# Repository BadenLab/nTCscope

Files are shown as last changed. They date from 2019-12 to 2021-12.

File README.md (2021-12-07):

<p align="right">
<h1 align="center">nTC(DBO)-Scope</h1></p>
<h4 align="center">An open source and ultra-low-cost design for large 3D field of view 2-photon microscopy</h4>
<p align="center"><h6 align="right">by F.K.Janiak and colleagues, University of Sussex, UK </h6></p>

This project is licensed under the [GNU General Public License v3.0]

Non-Telecentric 2P two-photon microscopy for 3D random access mesoscale imaging 

FK Janiak, P Bartel, R Bale, T Yoshimatsu, E Komulainen, M Zhou, K Staras, LL Prieto-Godino, T Euler, M Maravall, T Baden

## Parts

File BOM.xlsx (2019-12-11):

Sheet: Sheet1
 | Name | Code | Provider | Unit price | Total price | Number | comments | Source
DBO modifications | L1 | VISIR 1534SPR136 | Leica | £0.00 | £0.00 | 1 | custom modified
 | L2 | LA1229 | Thorlabs | £15.75 | £15.75 | 1 |  | https://www.thorlabs.com/thorproduct.cfm?partnumber=LA1229
 | L3 | LA1708 | Thorlabs | £15.60 | £15.60 | 1 |  | https://www.thorlabs.com/thorproduct.cfm?partnumber=LA1708
 | L2 and L3 holder |  |  | £0.00 | £0.00 | 1 | custom 3D printed
ETL Optomechanics | ETL | EL-16-40-TC-20D | Optotune | £682.00 | £682.00 | 1 | 790 Euro - this price constantly changes. Pretty much any similar ETL can be used
 | ETL mount cage | CXY2 | Thorlabs | £157.90 | £157.90 | 1 |  | https://www.thorlabs.com/thorproduct.cfm?partnumber=CXY2
 | ETL mount cage | SR8 | Thorlabs | £9.90 | £39.60 | 4 |  | https://www.thorlabs.com/thorproduct.cfm?partnumber=SR8
 | ETL mount cage | CPVM | Thorlabs | £34.91 | £34.91 | 1
 | micocontroler | Arduino due | Arduino | £35.00 | £35.00 | 1 |  | https://store.arduino.cc/due
ETL driver | driver board | PCB board | Eurocircuits | £22.05 | £22.05 | 1 | custom design, price for 3 ordered | https://eurocircuits.com
 | zener diode | 1N5359B | ON Semiconductor | £0.39 | £0.39 | 1 |  | https://www.mouser.co.uk/ProductDetail/ON-Semiconductor/1N5359BG?qs=y2kkmE52mdOH2DdJ0ygiPA%3D%3D&vip=1
 | 330 Ohm resistor | OX331KE | Ohmite | £1.42 | £1.42 | 1 |  | https://www.mouser.co.uk/ProductDetail/Ohmite/OX331KE
 | 1k | OX102KE-B | Ohmite | £1.42 | £1.42 | 1 |  | https://www.mouser.co.uk/ProductDetail/Ohmite/OX102KE-B
 | op amp | CA3140EZ | Renesas / Intersil | £2.06 | £2.06 | 1 |  | https://www.mouser.co.uk/ProductDetail/Renesas-Intersil/CA3140EZ?qs=cbl4%252BYHJGOH17873DHUGkQ%3D%3D&vip=1
 | 1k Ohm potentiometer | 534-1-1-103 | Vishay | £12.70 | £12.70 | 1 |  | https://uk.rs-online.com/web/p/potentiometers/8509794/
 | power supply +12V 0.42A | VEL05US120-UK-JA | XR Power | £5.32 | £5.32 | 1 |  | https://www.mouser.co.uk/ProductDetail/XP-Power/VEL05US120-UK-JA
 | transistor | N6039G | ON Semiconductor | £0.49 | £0.49 | 1 |  | https://www.mouser.co.uk/ProductDetail/ON-Semiconductor/2N6039G
 | 10 ohm resistor | OY100KE | Ohmite | £1.96 | £3.92 | 2 |  | https://www.mouser.co.uk/ProductDetail/Ohmite/OY100KE
 | BNC cable 0.5 m | 426-2038 | RS PRO | £9.22 | £9.22 | 1 |  | https://uk.rs-online.com/web/p/products/4262038/
Pockel cells control (optional) | Potentiometer controller box |  |  |  |  |  | coming soon!
 | Microcontroller | Arduino due | Arduino | £35.00 | £35.00 | 1 |  | https://store.arduino.cc/due
 | BNC cable 0.5 m | 426-2038 | RS PRO | £9.22 | £18.44 | 2 |  | https://uk.rs-online.com/web/p/products/4262038/
 |  |  |  | TOTAL | £1093.19

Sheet: Sheet2
1 | 11.66 | 2.02 | 19.53 | 1.78
2 | 12.07 | 2.05 | 19.28 | 2.12
3 | 12.07 | 2.1 | 19.16 | 2.04
4 | 12.24 | 2 | 19.41 | 2.29
5 | 12.01 | 2.03 | 19.28 | 1.88
6 | 11.78 | 2.11 | 19.28 | 2.1
7 | 12.01 | 1.96 | 19.28 | 2.12
8 | 11.89 | 2.07 | 20.12 | 2
9 | 11.95 | 2.43 | 19.41 | 2.02
10 | 12.07 | 2.1 | 19.53 | 2.06
av | 11.97 | 2.09 | 19.43 | 2.04
std | 0.16 | 0.12 | 0.26 | 0.13
 | 1.306695911 | 5.899856856 | 1.322101798 | 6.472056003

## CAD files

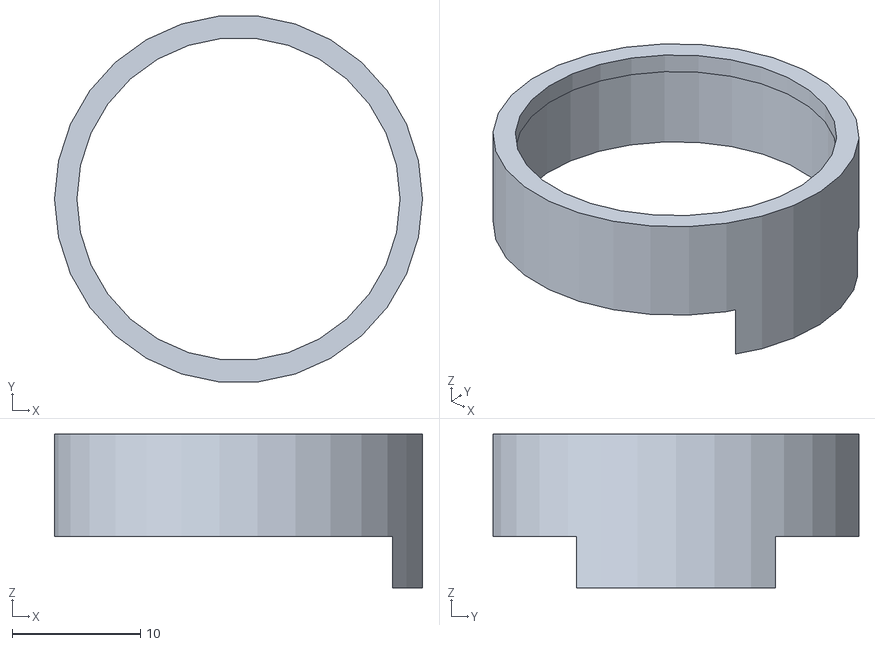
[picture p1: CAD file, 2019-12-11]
3D print/Lens_holder.stl
28.7 x 28.5 x 12.0

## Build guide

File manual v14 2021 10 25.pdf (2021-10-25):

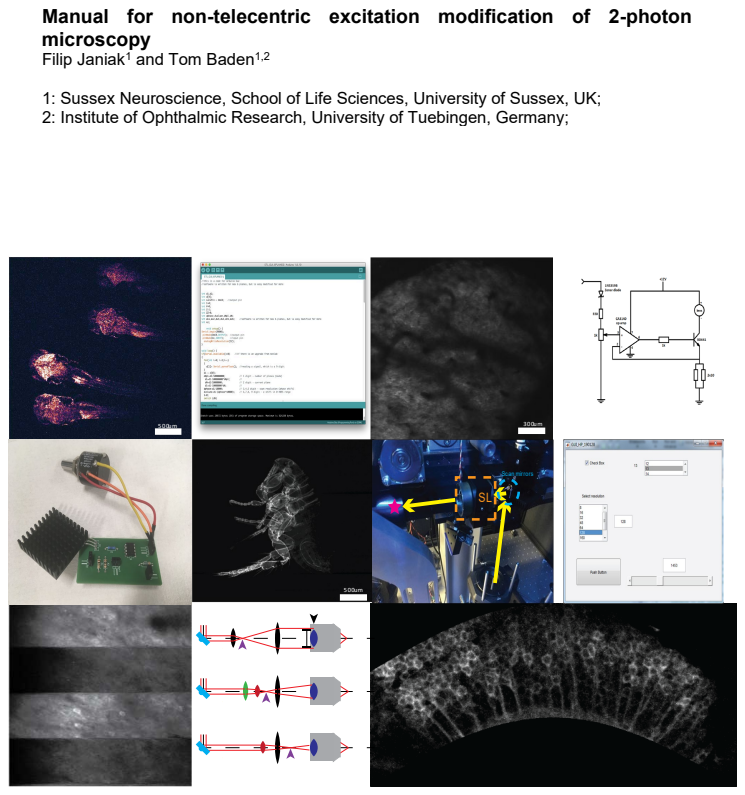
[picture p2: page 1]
Scan mirrors

Manual for non-telecentric excitation modification of 2-photon
microscopy
Filip Janiak¹ and Tom Baden¹,2
1: Sussex Neuroscience, School of Life Sciences, University of Sussex, UK;
2: Institute of Ophthalmic Research, University of Tuebingen, Germany;

A note on safety
Remember to always wear safety googles when working with lasers! Take off all hand-worn jewellery and watches as these might reflect the beam into your or someone else’s eyes. Always work at the lowest possible laser power. And never, even with the safety glasses on, look straight into the laser beam!

What will be useful?
Tape measure, fixed fluorescence sample (i.e. a test-slide), laser viewing card

Definitions and helpful simplifications
Many of the optical elements in 2p microscopes, like the scan lens (SL), tube lens (TL) and objective (objective lens) tend to consist of multiple stacked lenses with different curvatures and thickness. For simplicity, we treat each of these as a single ideal lens.

In detail: There is a large set of parameters describing optical properties of such lenses, however for us important are only the following: principal planes (P, P’), focal planes (F, F’), surface vertices (V, V’), and three focal lengths: effective focal length (EFL), back focal length (BFL) and front focal length (FFL). For details on any of these, see also the following Wiki articles:
https://en.wikipedia.org/wiki/Cardinal_point_(optics) https://en.wikipedia.org/wiki/Focal_length

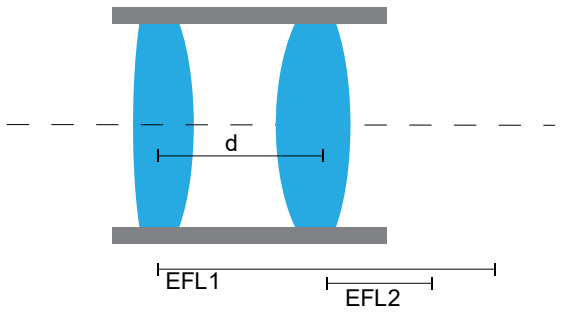
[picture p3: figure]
EFL1; EFL2
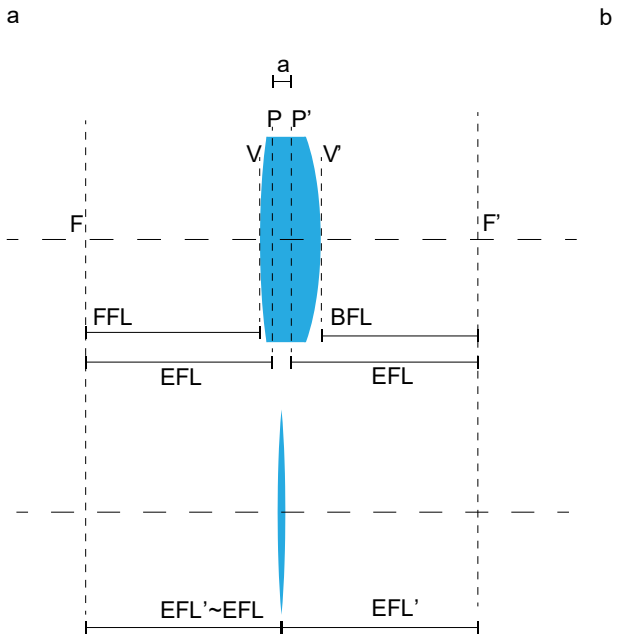
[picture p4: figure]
FFL; BFL; EFL; EFL’~EFL; EFL’
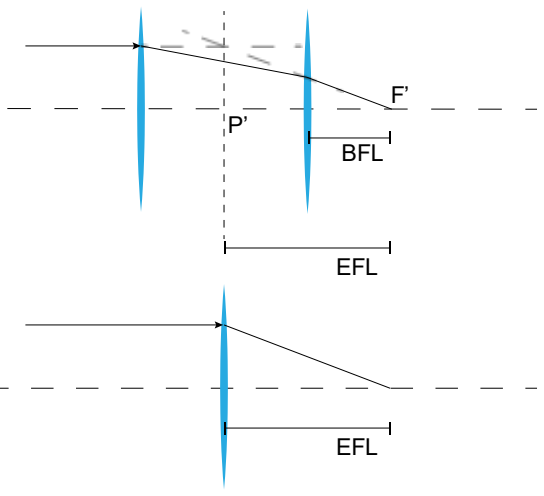
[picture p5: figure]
EFL; BFL

Fig 1. Thin lens approximation of a thick lens (a). Single thin lens approximation of two thick lenses (b).

In optical models, such constituent lenses can be replaced by a single, thin, ideal lens, and for simplicity this is what we are doing in all calculations and diagrams. This ideal lens has a negligible thickness, so principal points are located exactly in a centre of the lens, and effective, back and focal length are the same, and equal to EFL of thick lenses corrected by half of the thickness (EFL’ on fig 1). Typically, the thickness can be disregared if EFL>> thickness.

# EEEELL′ = EEEE +

aa

# 2 iiii (EEEE ≫ aa) EEEELL′ ≅ EEEE

To calculate effective focal length of two thin lenses, we can use:
1

# EEEE = 1

## EEEE 1

+

1

## EEEE 2

− dd

# (EEEE 1)(EEEE 2)

Or just simply:

1 = 1
1

+

1
2

− dd
1 2

See more on https://physics.stackexchange.com/questions/247617/how-is-focal-length-defined-for-a-two-lens-system-separated-by-a-distance-d (https://physics.stackexchange.com/questions/247617/how-is-focal-length-defined-for-a-two-lens-system-separated-by-a-distance-d)
This ideal lens is located in the back principal planes of complex lenses (which is usually in the centre of a given tube).

Initial steps: Obtaining all the key numbers of your specific setup.

This section is intended to help identify all key elements in your laser path between the scan mirrors and the sample plane, and to obtain concrete values for their relative distances and focal lengths etc..
1. Identify scan lens (SL). It should be the first lens ensemble after the scanning mirrors (from point of view of the laser source). Identify Tube Lens (TL), it should be the next one after SL. Measure the distance between them (D2).
2. If focal lengths and dimensions are unknown, carefully take out both lenses. Use gloves to avoid leaving smear-marks, and do not scratch them. Measure their focal distance (FSL,FTL), and their dimensions (ØSL, ØTL), for example as demonstrated here:

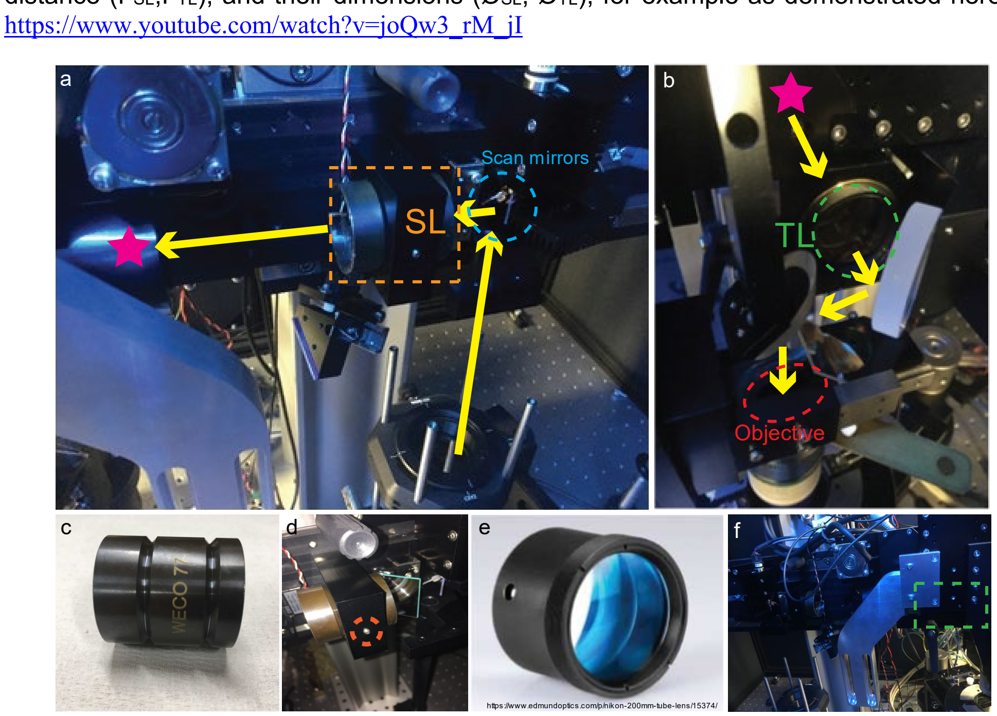
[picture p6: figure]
https://www.youtube.com/watch?v=joQw3_rM_jI; https://www.edmundoptics.com/p/nikon-200mm-tube-lens/15374/; Scan mirrors; Objective

Fig 2. Sutter MOM setup with DL standard configuration. Location of SL (a), TL and objective (b). SL outlook (c) and mounting (d). TL outlook (e) and position from the side (f).
If you use a Sutter MOM setup, the SL model is VISIR 1534SPR136 from Leica (Fig. 2a), which is mounted in a WECO 77 tube (Fig. 2c). It has a focal length of 50 mm, and it is located 56.6 mm from second scan mirror. The thickness of the lens (which is made up of two biconvex lenses) is 43.1 mm. The external tube diameter is 38.2 mm, and the internal aperture diameter is 28.9 mm. It is easy to unscrew and take out (Fig. 2d). However, in the Sutter MOM the TL (MXA22018, Nikon) is less readily accessible (Figs. 2b,f). It has a 200 mm focal length (Fig. 2e) and is positioned at a distance of 250 mm from the SL. The length of the TL tube is 29 mm, and it has a 36 mm aperture.
3. For your objective, check the magnification, nominal working distance, and size of the back aperture (Øobj). Measure the total distance between the objective’s back aperture and the SL.

Note: Microscope objectives are designed to correct for chromatic aberration at a specific distance D3 between TL and its back aperture OBA. For Zeiss objectives, D3 = 95 mm. (Philbert S. Tsai and David Kleinfeld, 2009).
In our setup, we use a Zeiss Objective W "Plan-Apochromat" 20x/1.0, 1.8 mm working distance.
In a standard diffraction limited (DL) configuration, the distance between SL and TL is equal to the sum of their focal distances D2=FSL+FTL. D3 is specified by the objective as discussed above.
4. Based on these numbers, calculate the distance D1 between the second scan mirror pivot point and SL that minimizes motion of laser beam (intensity fluctuation) on

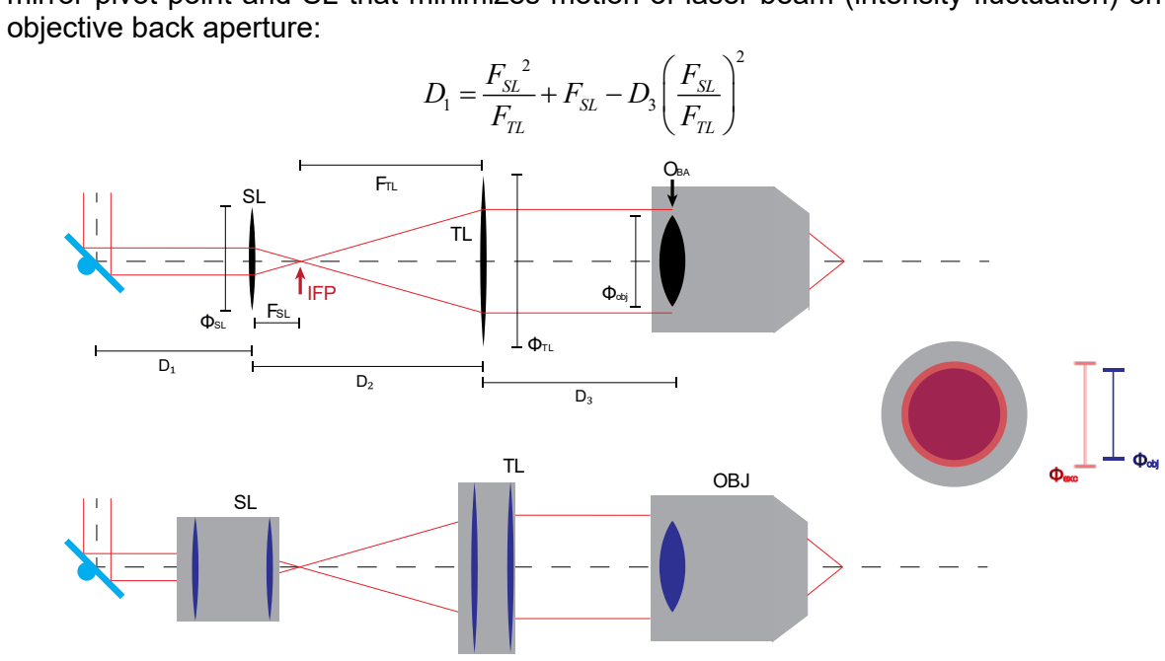
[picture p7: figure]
objective back aperture:; FSL; FTL; ФSL; ФTL; Фobj; OBA; IFP; OBJ

Figure 3. DL configuration. Ideal lenses approximation (top), objective back aperture overfilling (left) and typical configuration with stacked lenses (down).

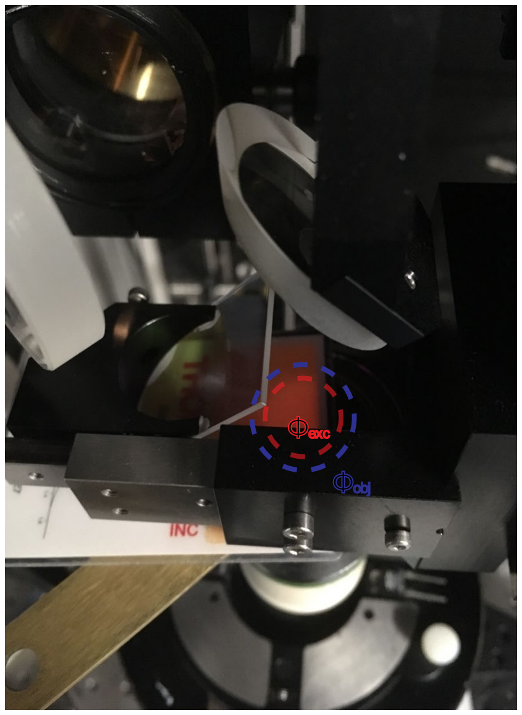
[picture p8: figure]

5. Check objective’s back aperture (OBA) filling factor (Øexc/Øobj). To do so, turn on a regular scan mode at “high zoom” (i.e. with minimal movement of scan mirrors) without the objective in place. Use a laser viewing card in the position where the objective’s back aperture would be to assess the setup’s fill factor (i.e. the size of the laser spot relative to the objective’s back aperture) (Fig. 3, 4). Alternatively, if your laser supports an alignment mode at a visible wavelength (typically low 700s of nm) you can also do this procedure with a piece of paper in place of the laser viewing card.
In a DL configuration, overfilling OBA by the excitation laser beam minimizes the lateral and axial size of the excitation spot (point spread function, psf), but also decreases effective excitation power delivered by the objective (Helmchen & Denk, 2005; Philbert S. Tsai and David Kleinfeld, 2009).

This manual describes how to change a setup from a DL configuration. Therefore, based on your data, check and calculate if your setup operates on DL settings.
If it is, go ahead to the next section. If it is not, try to understand why. There are two main possibilities. First, unintentional misalignment during a construction/mainlining or a using of the setup, which can be easily fixed to come back to DL configuration or apply a modification. Second, intentional changes from DL configuration. In this case you need to check why your setup is designed in this specific manner (e.g. if there are specific advantages/limitations). In this case, application of our modifications could be more complicated, but may still be possible.

We present two modifications to obtain a divergent excitation 2-photon setup leading to an expanded field of view (FOV) and excitation spot (point spread function, psf).
Throughout, we will be focussing on two parameters: Intermediary focal point (IFP) and the objective’s back-filling factor (Fig. 5):
Intermediary focal point (IFP) position | Objective back aperture filling factor

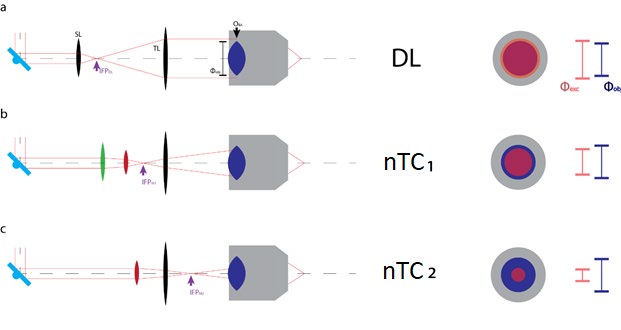
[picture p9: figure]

## nTC1 configuration

1. For “non-telecentric modification 1” (nTC1), the goal is to move the IFP closer to the TL, yet without passing it, while simultaneously underfilling OBA (Fig. 6).
2. To assess the extent of any changes, use a fixed fluorescence sample. Prepare your setup for a standard experiment with DL configuration. Using lowest possible power find a suitable sample plane (one with obvious structure) and determine the original maximal FOV and working and working distance (e.g. by moving the sample side to side and checking when a particular image structure leaves the field of view).
3. Prepare setup to measure objective back aperture (OBA) filling factor (Øexc/Øobj) – see initial steps.
4. Completely remove SL from the system. Before implementing any modifications, remember to switch off the laser!

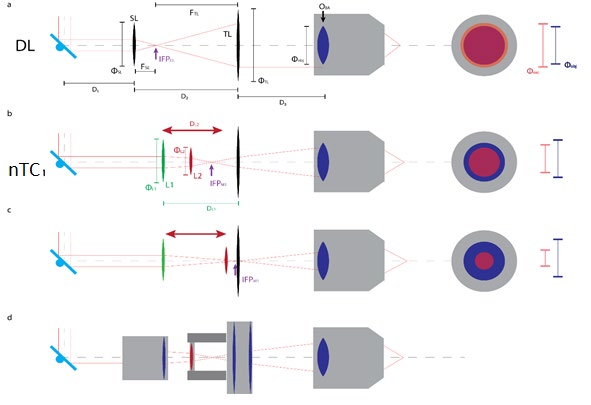
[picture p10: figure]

Sidenote: Why not simply shift the original SL? We can of course move the IPF closer to TL by simply shifting forward the SL. However, this will increase overfilling OBA (we are hoping to decrease this) which in turn will decrease effective excitation power on the sample plane (we are hoping to increase this).

L2 and in result different FOV and psf shape. (d) shows configuration (b) without thin lens approximation.
5. Insert new lenses in place of the SL. In our tested nTC1 solution for the Sutter MOM, we use 2 lenses in place of the SL: L1 and L2, with focal lengths 190 and 175 mm, respectively.

In our implementation, L1 is a modified Sutter MOM SL - VISIR 1534SPR136, Leica (Fig. 7b), and L2 is LA1229 from Thorlabs (Fig. 7c). This specific choice for L1 is one of convenience, but it can be equally be replaced by a new 190 mm lens.
nTC1 can also be achieved using a single lens. However, in this case, the OBA filling factor will be much smaller and difficult to control, and the psf will disproportionately inflate already for a small FOV increase.
For mounting L1, we use the original SL mount (as our L1 is a modified SL). For assembling and shifting L2, we use a 3D printed lens holder that fits into the existing tube that also holds the TL at its end (Fig. 6a). The 3D printable file Lens_holder.stl is found on our GitHub.

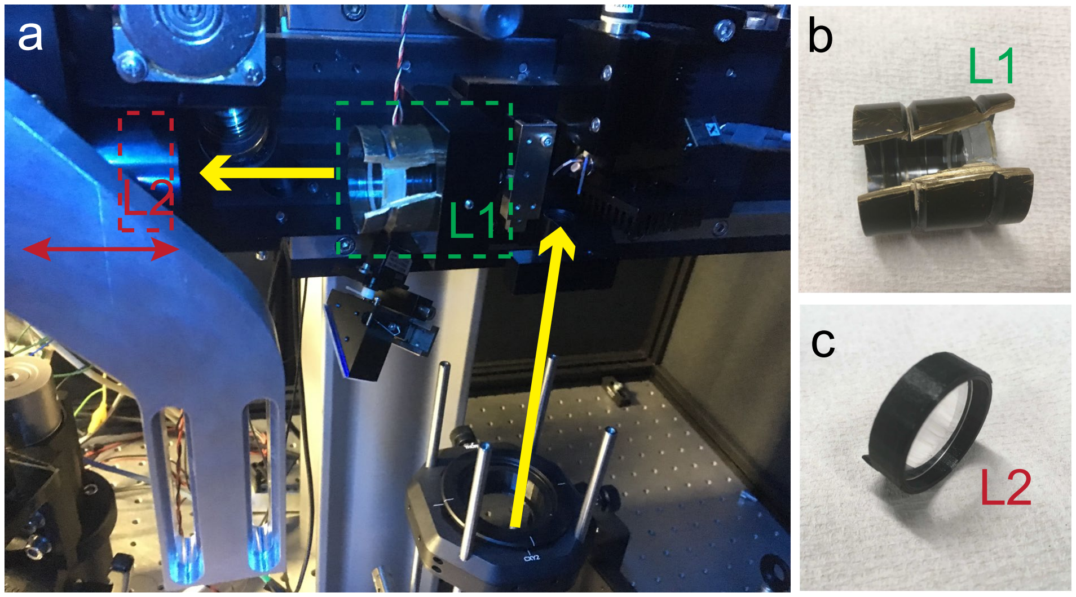
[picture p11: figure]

Fig 7. Sutter MOM setup with nTC1 configuration. Location of L1 and L2 (a), L1 modified from Leica VISIR 1534SPR136 (b), L2 with custom design 3D printed holder (c)
6. Select the “right” L1 and L2 lenses for your setup.
Sketch out how you want the optical configuration of your setup to look like. Note original SL, TL and their apertures. Note existing holders for lenses and the physical constraints imposed by your setup’s mechanics to position and shift L2.

For L1, use a lens with a focal distance FL1 = DL1, such that by itself, L1 sets up an IFP exactly at the centre of the TL. We use a 190 mm lens, positioned 190 mm in front of the TL.

If desired, you can also use an L1 with shorter or longer focal distance than DL1. However, if the focal distance is shorter, the range of FOV changes generated by shifting of L2 position decreases. In contrast, of L1 focal distance is longer than DL1, it will bring the IFP behind the TL, effectively resulting in nTC2 (discussed below). In this case we can shift between modification 1 and 2 mode by change a position of L2.
Make sure that the aperture (diameter) of L1 is suitable. It should be in similar range as the original SL (ØL1 ≈ ØSL) to make sure the incoming laser beam does not get clipped on the edges during scanning.
For L2, the focal length (FL2) should be in the range between FL1 and FL1/2. FL2 shortening introduce an overfilling of OBA, or even TL aperture, resulting in power lost and fluctuation of excitation intensity on FOV. FL2 extending decrease range of IFP and (Øexc/Øobj) changes.

On our setup, we use a 175 mm FL2, which is shifted along the laser path between 100 and 5 mm from TL.
Ultimately, the exact position vale of FL2 as well as the position of L2 relative to L1 and TL will dictate the position of the IFP, and thereby set the (Øexc/Øobj) factor, FOV and the size of the excitation psf.
If possible, choose an aperture of L2 that is similar to the one for L1 (ØL1 ≈ ØL2). In our case it was not possible to use the exact same size, so we used the largest possible L2 diameter (25,5 mm) which just about fit into the 3D printed holder that was slotted into the tube that also held the TL.
7. Test the result of your changes and establish the range of FOV shifts achievable by shifting L2 up and down the laser path. Start by setting L2 as close as it is possible to L1 and take a scan of your fixed sample. Likely, working distance will be longer than in the original DL configuration so you will need to refocus. Note the difference of a working distance and check the maximal FOV size. Also, zoom in to assess spatial resolution. Now, shift L2 closer to TL and again check FOV and working distance. Both should increase. Note the range of changes that can be achieved with this configuration. Remember to shift L2 only when you are not scanning and your laser is disabled!

If you find that working distance and FOV starts to decrease again at some point when shifting L2 closer to TL, it means that L2 is further away from L1 compared to L1’s focal distance. In this case, put L1 closer to TL or exchange it for the one with longer working distance.

8. As for 7, also check the objective filling factor (Øexc/Øobj) for a different positions of L2 (see initial steps paragraph). Shifting of L2 towards TL will increase underfilling (i.e. will make the laser spot smaller at the level of the objective’s back aperture), and should result in an expansion of the psf.

If desired, you can try to keep a (Øexc/Øobj) constant even with increasing FOV by exchanging of L2 for one with shorter working distance as you shift it closer to TL. This effectively allows setting FOV somewhat independently of psf expansion (up to a point). Sidenote: Remember that overfilling of OBA will reduce effective excitation power, and can also lead to uneven excitation power across the FOV.
9. As desired, you can also directly measure the excitation psf, for example by imaging fluorescent beads embedded in agarose. When doing so, remember to keep laser wavelength and excitation power at the sample plane approximately constant to ensure fair comparison (measured psf dimensions strongly depend on these factors). Note that excitation power at the sample plane should also increase as you decrease Øexc/Øobj, so it is best to directly measure this on the sample plane using a power meter.

## nTC2 configuration

1. In nTC2, goal is to move the IFP beyond the TL (but still in front of OBA), again while ensuring underfilling of OBA (Fig. 7). Most steps to set-up nTC2 are very similar to those required to set up nTC1. Therefore, first consult the description in nTC1. From here, implementation nTC2 will be straightforward:
2. Starting from a nTC1 configuration, remove L1 from the setup and replace L2 with L3. (If you start from a DL setup, simply remove the SL entirely, and find a way to mount L2/L3 in front of the TL).

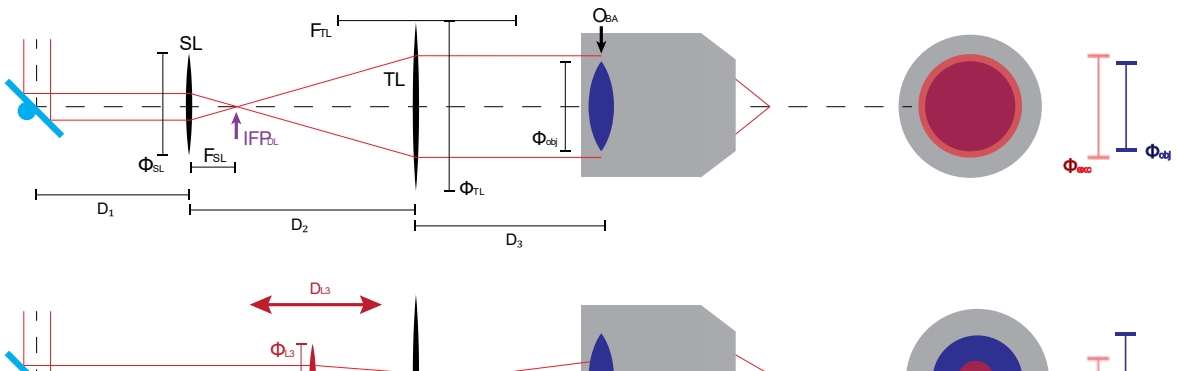
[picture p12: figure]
FSL; FTL; ФSL; ФTL; Фobj; OBA; IFPDL

Fig 8. Optical design of DL(top) and versions of nTC2 configurations (below). Left: positions of the lens(es), right: objective back aperture filling factor. Different positions of L3 and in result different FOV and psf shape. Bottom row shows configuration without thin lens approximation (see introductory definitions). To compare with nTC1 check Fig 6.

3. How to select L3? The goal of L3, depending on its position in front of TL, is to shift the IFP anywhere between the TL and OBA. In our setup we use a 200 mm focal length Ø1 plano convex lens (LA1708, Thorlabs) which is probably a good starting point for most optical configurations. L3 is assembled exactly like L2 in nTC1, using a 3D-printed holder. In our configuration we can slide it anywhere between just next to the TL and up to 10 cm in front of it.

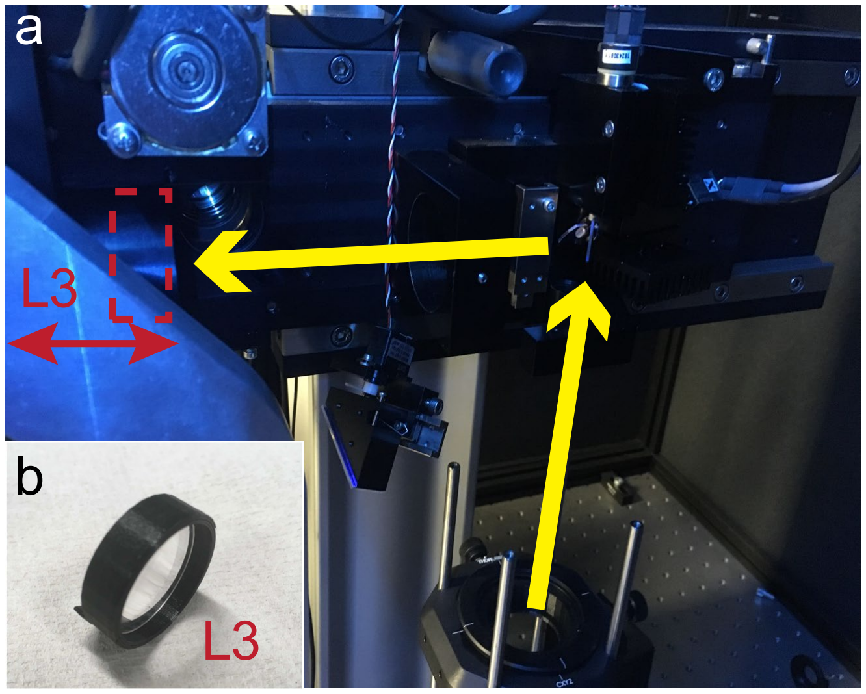
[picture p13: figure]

Side note: If you remove all lenses except the TL and Objective (i.e. remove SL/L1/L2⁽*)), your parallel beam coming from the scan mirrors should come into focus beyond the objective back aperture (FTL is always bigger than D3). Accordingly, OBA will be illuminated by convergent beam. However, we want the beam to diverge, so you will need a L3 lens that is powerful enough to generate an IFP (just) before the laser beam reaches the objective.
Check always that the beam reaching the OBA is divergent, not convergent (for example with a laser viewing card).
Throughout, when choosing new lenses, make sure they have high transmission efficiency in the infrared range such that the laser beam does not get attenuated too much.
Remember to use the highest possible aperture of the lens. Of course, this factor will be limited by space in Your scope (in our cases size of the tube where L3 is moved. Selection of a too small aperture will likely result in inefficient collection of the excitation beam after the mirrors (as now there is no longer a SL to direct the beam onto L3).

Electrically Tunable Lens
In our setup we implemented an Electricaly Tunable Lens (ETL) for rapid axial focussing. Our ETL is an EL-16-40-TC20D, Optotune, controlled by a custom driver and custom written software (see GitHub).
ETL Optics

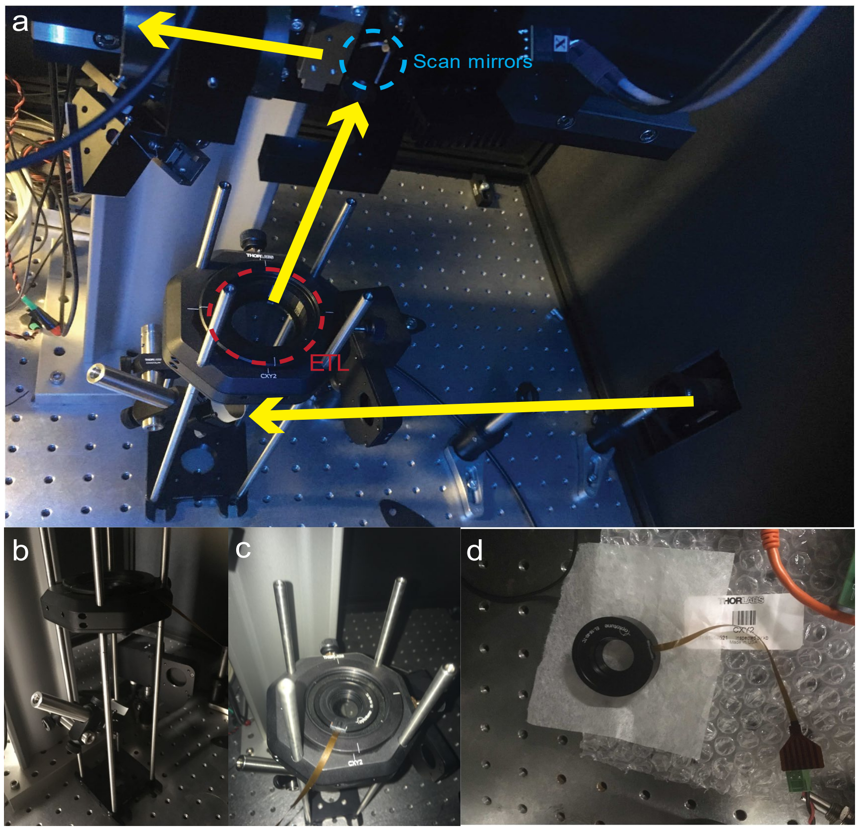
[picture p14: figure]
Scan mirrors; ETL

Fig 10. Sutter MOM setup with cage for ETL (a). View of the cage with ETL holder, and mirror reflecting excitation beam to scan mirrors (b), ETL on the holder (c) and ETL EL-16-40-TC20D by itself (d).
In our approach, we decided to use an ETL which operate in a range of -10 to +10 dpt. This means that it focuses from infinity (∞, no focus, parallel beam) to -10 cm for negative current and from ∞ to +10 cm for positive current. If the ETL is not supplied by any current, it does not strongly interfere light which is going through (according to the product manual, it introduces a negligible, long range focus).

The main idea is to locate the ETL far away from the objective (compare to original idea presented by Grewe (Grewe, Voigt, van ’t Hoff, & Helmchen, 2011)). By changing the ETL’s focus from infinity to a positive value (supply positive current) we can then introduce a small convergence into the excitation beam before it hits the scan mirrors. This effectively elevates the imaging plane under the objective. In our solution, we are operating around 25% of a maximum ETL power, which give us an effective focus shift of up to 600 µm.
On our setup, the ETL in mounted horizontally on custom cage build from Thorlabs elements (more details in bill of materials, BOM). Fig. 10a presents the layout of the ETL holder on our Sutter MOM setup. We replaced the Sutter MOM-s original tube with mirror (which bounces the excitation beam from below onto the scan mirrors) by our cage including a new mirror. This new mirror can be adjusted in xyz directions, and in reflection angles, to help setup a perfectly vertical beam. The ETL holder is adjustable in x and y, and is located 20 cm below the first scan mirror.

ETL driver hardware

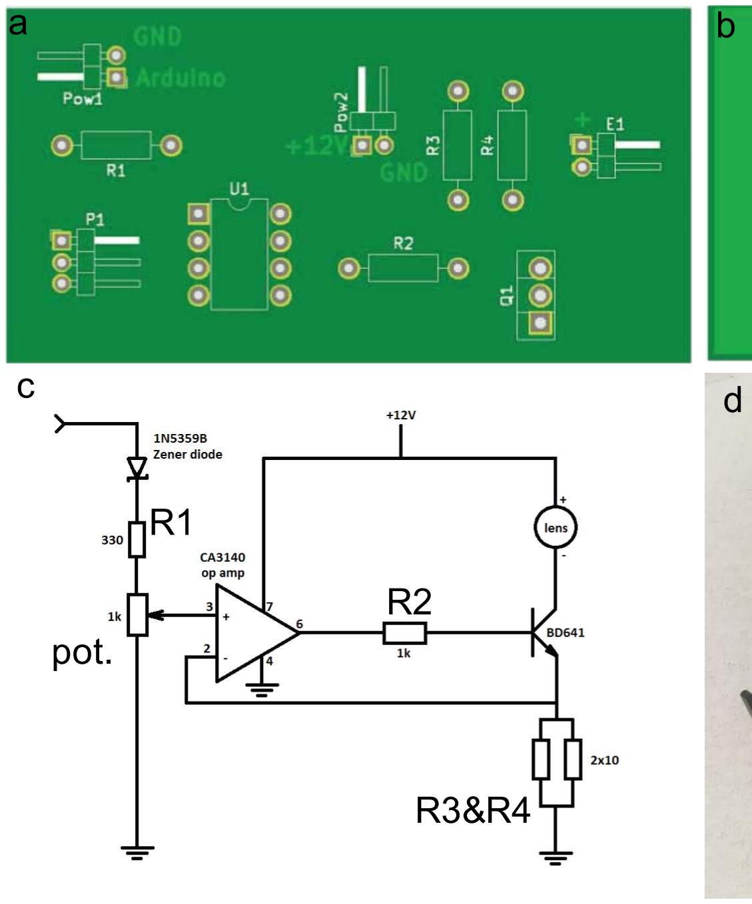
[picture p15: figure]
pot.
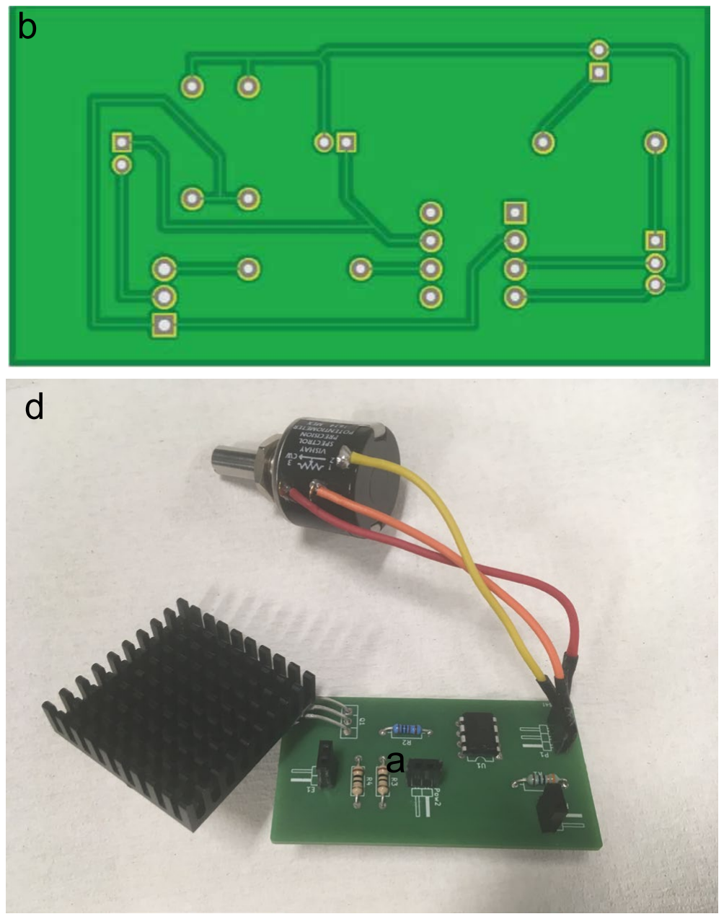
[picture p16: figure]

Fig 11. Top (a) and bottom (b) view of ETL driver printed circuit board (PCB). Schematic of electrical circuit (b) and photograph of the assembled driver (d). The Gerber files for producing the PCB are available on the project GitHub.

To control our ETL, we are using a custom designed current driver combined with an Arduino Due microcontroller. The driver’s overall goal is to generate ETL command signals that are line-synchronised with the 2-photon scan engine. For this, the Arduino Due reads a line-signal from the scan engine (e.g. a copy of the fast-mirror command, or a line-synchronised TTL pulse) to count lines. For this, the Arduino is reading such as signal on Analog pin A1. In our case, this signal is simply a copy of the “banking signal” which we send to the Pockels Cell during the scan retrace (the latter is an optional “trick” to reduce bleaching during retrace times, this has been discussed previously e.g. in Euler et al. 2009 Pflueger’s Archive).
Upon reading this signal, the Arduino “counts scan lines”, and executes driver commands accordingly, based on a custom script controlled from a Matlab GUI (below). For this, the Arduino sends a driving signal through its Digital-Analog-Converter (DAC) output port into the custom driver board. On the Arduino side, this DAC signal is ranges from 0 to 4,095 (12 bit), which corresponds to a voltage range of 0.55 - 2.75 V, which serves as the sole scan input to the custom driver board. First, the 0.55 V offset (corresponding to 0 on the Arduino) is removed using an operational amplifier (op-amp). Next, the remaining signal is scaled using a potentiometer which allows defining the maximum current sent to the ET (which also indirectly defines its resolution). Finally, this signal is used to open a negative-positive-negative (NPN)-transistor, which works as a switch for a current from a separate +12V 0.42 A power supply.

Note that our current driver works only for a positive current, even if our ETL works also for the negative.
Note that we are using an additional Zener diode as a connector between Arduino output and our current driver input. Reason of using it was additional protection of current driver and ETL because of problems with series of unstable Arduino boards which we have been using (some of them temporary didn’t work properly). This Zener diode introduce additional voltage drop to the system, so it doesn’t need to be done on op-amp.
Figure 11a and b shows the PCB of our driver. PCB file ETL_driver_board.kicad_pcb is available for download on our GitHub. In addition, you will need the following electronic components (full details on BOM):
- Zener diode (1N5359B) (additional used as connector between Arduino and driver board – see note above),
- R1 330 Ω,
- 1kΩ potentiometer,
- Op-amp CA3140EZ,
- R2 1 kΩ,
- R3&R4 10 Ω.
- N6039G transistor
- 12 V 420 mA power supply.

All connection pins are labelled on the board (Arduino, +12, + (ETL), and GND for Arduino and power supply). The Pin next to + is a negative connection for ETL.

Note that in addition we attached a heat sink to the N6039G transistor which helps to dissipate heat if the driver is operated for prolonged periods of time (see photo in Fig. 11d).

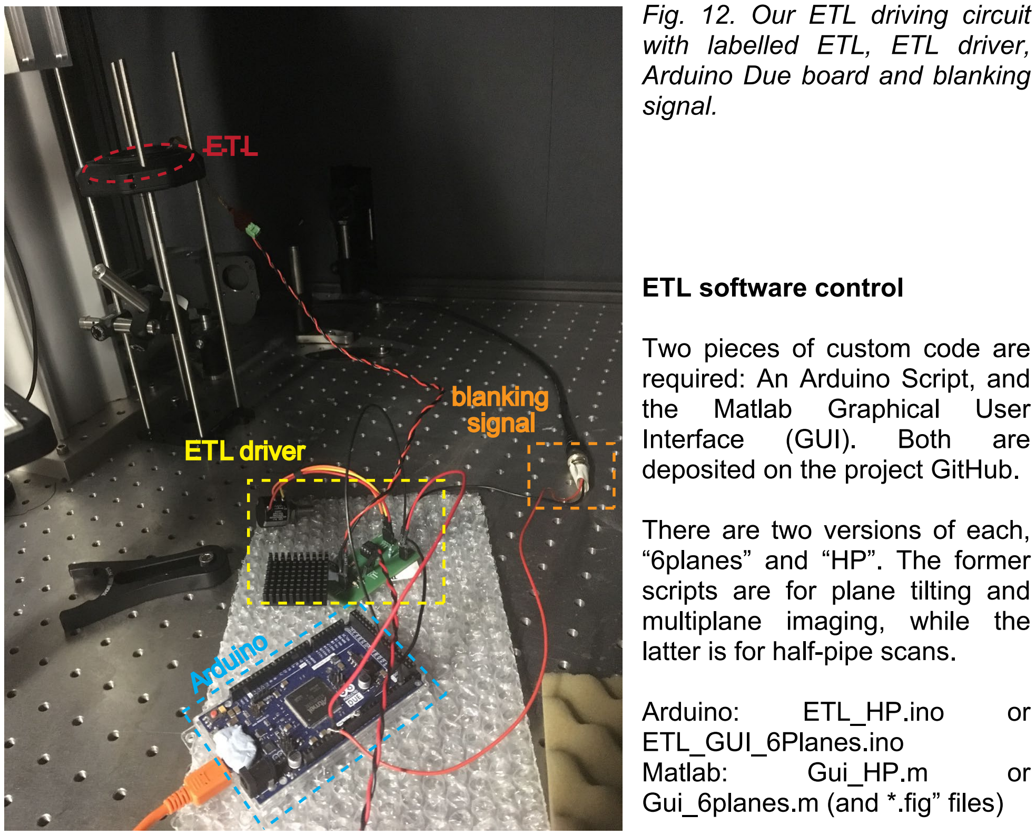
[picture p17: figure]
Fig. 12. Our ETL driving circuit with labelled ETL, ETL driver, Arduino Due board and blanking signal.; ETL software control; Two pieces of custom code are required: An Arduino Script, and the Matlab Graphical User Interface (GUI). Both are deposited on the project GitHub.; There are two versions of each, “6planes” and “HP”. The former scripts are for plane tilting and multiplane imaging, while the latter is for half-pipe scans.; Arduino:; ETL_HP.ino; ETL_GUI_6Planes.ino; Matlab:; Gui_HP.m; Gui_6planes.m (and *.fig” files)

Our software control is fully independent from the software used to control the 2P microscope (e.g. ScanImage, or in our case ScanM), meaning that it can in principle be seamlessly integrated with any working 2p system so long as a line-synch signal is available to be read by the Arduino.
To communicate with the Arduino and upload the script, download the Arduino integrated development environment (IDE). The Arduino IDE is freely available at https://www.arduino.cc/en/main/software. Tutorials on how to connect the Arduino via serial link and upload scripts are widely available online, so we will not cover this step here. You only have to upload the script once (the Arduino stores it locally), but you will need to keep the Arduino connected to your computer prior to changing any scan configuration so as to allow the Matlab script to communicate with it (see below).
Our GUI is written in MATLAB (Mathworks), which is widely using in academia. If you do not have it on your computer, check if your institution has a licence for it. There is also a 30-day free trial version https://uk.mathworks.com/products/matlab.html.

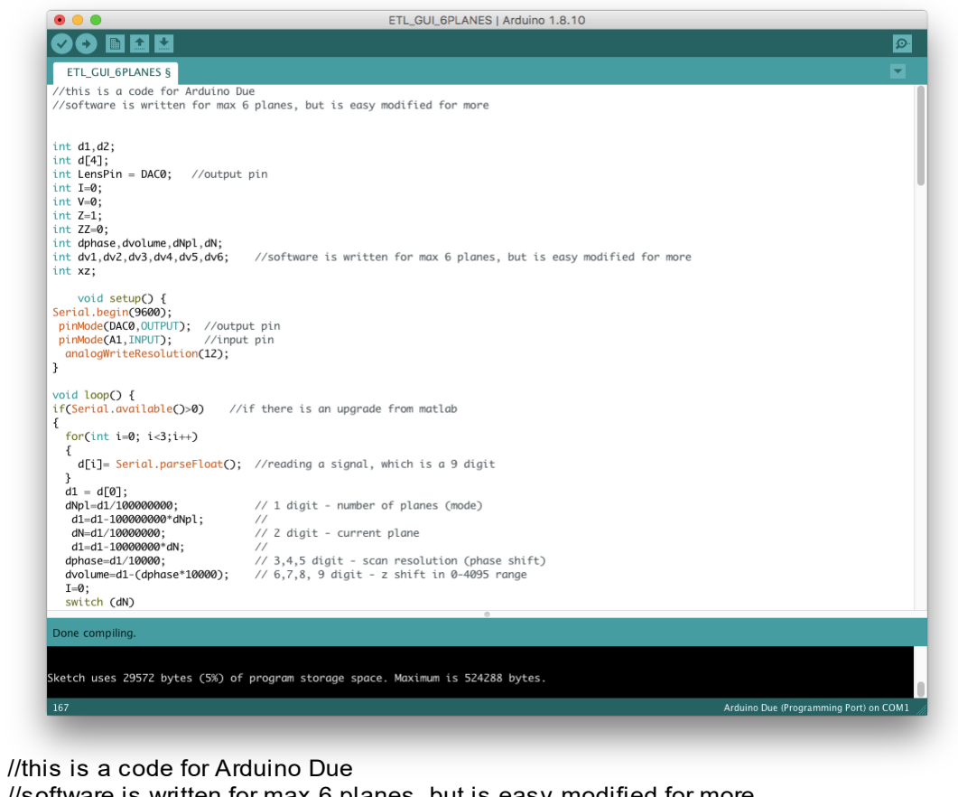
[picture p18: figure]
//this is a code for Arduino Due

//software is written for max 6 planes, but is easy modified for more

int d1,d2;
int d[4];
int LensPin = DAC0; //output pin
int I=0;
int V=0;
int Z=1;
int ZZ=0;
int dphase,dvolume,dNpl,dN;
int dv1,dv2,dv3,dv4,dv5,dv6; //software is written for max 6 planes, but is easy modified for more
int xz;

void setup() {
Serial.begin(9600);
pinMode(DAC0,OUTPUT); //output pin pinMode(A1,INPUT); //input pin analogWriteResolution(12);
}

void loop() {
if(Serial.available()>0) //if there is an upgrade from matlab {
for(int i=0; i<3;i++)
{
d[i]= Serial.parseFloat(); //reading a signal, which is a 9 digit }
d1 = d[0];
dNpl=d1/100000000; // 1 digit - number of planes (mode) d1=d1-100000000*dNpl; //
dN=d1/10000000; // 2 digit - current plane
d1=d1-10000000*dN; //
dphase=d1/10000; // 3,4,5 digit - scan resolution (phase shift) dvolume=d1-(dphase*10000); // 6,7,8, 9 digit - z shift in 0-4095 range I=0;
switch (dN)
{case 1:
dv1=dvolume;
case 2:
dv2=dvolume;
case 3:
dv3=dvolume;
case 4:
dv4=dvolume;
case 5:
dv5=dvolume;
case 6:
dv6=dvolume;}
}
int sensVal=analogRead(A1); //reading blanking signal switch (dNpl)
{
case 1: //for xyz scans

if (sensVal+Z>1200){ // 1200 is a average noise value read from A1. PLEASE CHECK IF IT
IS | //CORRECT FOR YOUR SETUP
int xz=round(3*4095/dphase);
Z=1;
I=I+1;
}
V=I*dvolume;// z shift for xyz

if (I==dphase){
I=0;
}

case 2: // 2 planes

if (sensVal<10){
Z=200; //2Z=200 is a treshold value betwen HI and LOW of blanking signal for our setup. //PLEASE CHECK IF IT IS CORRECT FOR YOUR SETUP
}
if (sensVal+Z>1200){
Z=1;
I=I+Z;
}
if (I==dphase){ //change z volume no 1 V=dv1;
}
if (I==dphase*2){ //change z volume no 2 I=0;
V=dv2;
}
break;
case 3: | // 3 planes
if (sensVal<10){
Z=200;
}
if (sensVal+Z>1200){
Z=1;
I=I+Z;
}
if (I==dphase){
V=dv1;
}
if (I==dphase*2){

V=dv2;
}
if (I==dphase*3){
I=0;
V=dv3;
}
break;
case 4: // 4 planes
if (sensVal<10){
Z=200;
}
if (sensVal+Z>1200){
Z=1;
I=I+Z;
}
if (I==dphase){
V=dv1;
}
if (I==dphase*2){

V=dv2;
}
if (I==dphase*3){

V=dv3;
}
if (I==dphase*4) {

V=dv4;
I=0;
}
break;

case 5: // 5 planes
if (sensVal<10){
Z=200;
}
if (sensVal+Z>1200){
Z=1;
I=I+Z;
}
if (I==dphase){
V=dv1;
}
if (I==dphase*2){

V=dv2;
}
if (I==dphase*3){

V=dv3;
}
if (I==dphase*4) {

V=dv4;
}
if (I==dphase*5){
I=0;
V=dv5;
}
break;

case 6: // 6 planes
if (sensVal<10){
Z=200;
}
if (sensVal+Z>1200){
Z=1;
I=I+Z;

Fig 13. Arduino code with comments for multiplane and xyz imaging.

ETL software control: Multiplane and XYZ imaging
First, upload the Arduino script ETL_GUI_6Planes.ino (called a “Sketch” in Arduino) to the Arduino board. Once this is done, you can close the Arduino IDE.
Next, open MATLAB and launch Gui_6PLANES.fig and Gui_6PLANES.m (If you are unsure how to do this, look for an online tutorial how to launch code in MATLAB.). In short, put both files into a common folder, change the MATLAB path to this folder, and execute Gui_6PLANES.m. This should bring up the GUI (Fig. 14).
From within the MATLAB GUI, connect the Arduino. For this, select the serial (COM)-port to which the Arduino is connected (Fig. 14, list 1) (It will be the same that you previously used to upload the Arduino script - if you are unsure how to identify the Arduino’s COM-port, search for one of the many tutorials online). In our cases it happens to be COM 13. Note: ensure that the COM port is not busy – this can easily happen if the Arduino IDE’s serial monitor happens to the open, or if it is still uploading the script.
Next tick the “ETL ON” checkbox to connect to the ETL. This sets up an open serial communication between Matlab and the Arduino (this also means that you can no longer communicate with the Arduino from elsewhere, e.g. the Arduino IDE. So, if you want to upload e.g. a different Arduino script, you need to untick the ETL ON box again).
From here, you are ready to start using the ETL in synch with the scan commands. Remember, in our implementation, the ETL can only lift the imaging plane, so the lowest position of your desired scan should be defined by the actual objective position (ETL at position 0)
Search-z function. To statically change the z-plane of your scan, simply enter a value between 0-4,095 into window (3) and press button (4) to confirm. Each time you do this the GUI sends a command to the Arduino, which in turn will send a static driver signal to the ETL and thus shift the imaging plane. This function is useful to explore by hand which values entered into the GUI correspond to what kind of actual z-shift. Confirm that this works by running any xy-scan on your scan software and changing this number (you don’t need to stop the scan for this). It may take a few seconds for any change to take effect.

case 6: // 6 planes
if (sensVal<10){
Z=200;
}
if (sensVal+Z>1200){
Z=1;
I=I+Z;
}
if (I==dphase){
V=dv1;
}
if (I==dphase*2){

V=dv2;
}
if (I==dphase*3){

V=dv3;
}

if (I==dphase*4) {

V=dv4;
}
if (I==dphase*5){

V=dv5;
}
if (I==dphase*6) {
I=0;
V=dv6;
}
break;
case 7: // single plane shift for z seachhing V=dvolume;
break;
}
analogWrite(LensPin,V); //write value to current driver }

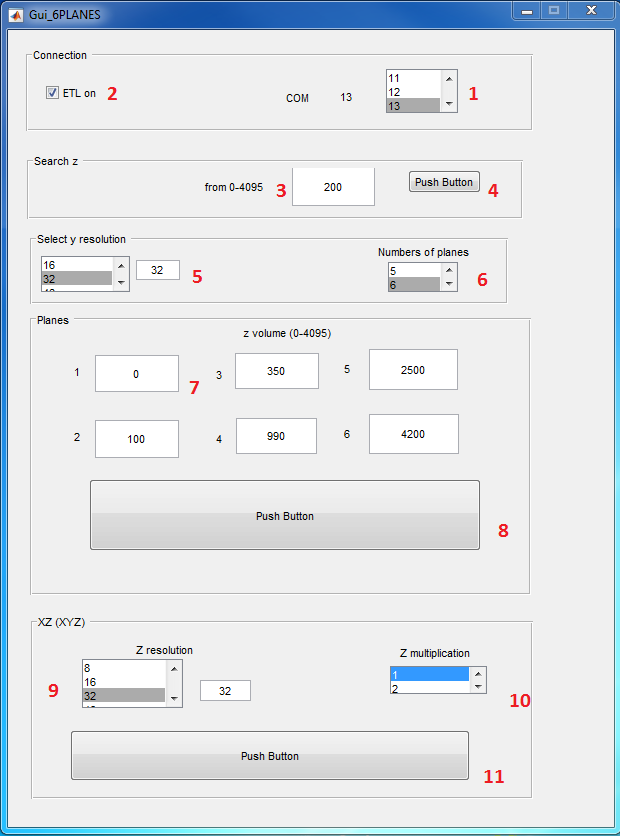
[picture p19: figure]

Fig 14. MATLAB GUI for the multiplane and xyz imaging.
Z-shift calibration (optional). Use a structured fluorescence sample (e.g. a test-slide) that allows you to easily identify specific structures at different imaging depths. Prepare your setup for standard 2P imaging, find a suitable image plane without engaging the ETL (ETL disconnected or set to “0”). Now, put the maximum allowed value of 4,095 into window (3), and push button (4). This should jump the imaging plane upwards, and potentially quite substantially so (in our case some 600 microns). Now go down in your sample using the objective and find the same imaging plane again. Take a note of the effective note the z-shift that you needed to use to compensate for the ETL. This is the maximum z-jump range possible with your configured optics and ETL-driver settings as defined by the potentionmeter (see driver). If this range is too small or too large for your purposes, rotate the potentiometer by a few turns and repeat the above. Once you are happy with the effective z-jump range, ensure that the dependency between the number entered into the GUI and the effective z-jump is approximately linear (it is very linear in our case, where we use ~25 max driving current on the ETL).
Scan-synchronised ETL commands. For any of the above procedures, the line-counting feature of our custom driver is not really used as the driver is just outputting static commands. However, for multiplane imaging, tilting the scan plane (xyz scans) or for halfpipe scans (see next chapter), the ETL must be synchronised to the scan mirrors with the line-synch connection (see driver chapter above).
Multiplane and staircase scans. Here, the control logic of our GUI is simple – for multiplane imaging it simply jumps the ETL to a new current (and hence effective focus position) once it counts a certain number of scan lines based on the values you enter under “select y resolution” and “Number of planes”. For example, if you choose a scan with 32 scan lines in your 2p control software (y = 32), you can then select 32 under “select y resolution” and the ETL will jump to a new plane every 32 lines, in perfect synch with the scan. Then you can define the number of planes. For example, if you choose 2 planes, it will execute 32 lines and depth 1, and then 32 lines at depth 2, and thereafter jump back to depth 1 etc.
Here, the specific depths it will jump to each time is defined in the window titled “planes”. Values entered in planes that are not used (e.g. plane 3 in a 2 plane configurations) will simply be ignored. For now, the GUI is configured for up to 6 planes to not clutter the GUI. However, it would be relatively straightforward for any experienced programmer to change this in the MATLAB code provided.
While this setup lets you set up straightforward multiplane scans, it can also execute some more “interesting” scan paths simply by playing with the numbers. For example, you can run a “step-scan” (i.e. half a scan at plane 1, and the other half in plane 2 – as for example shown for simultaneous eye-brain imaging in zebrafish in the accompanying MS). For this, taking our previous example, simply change the value of 32 to 16 under select y resolution. This will jump the ETL twice per frame and generate the intended effect).
Note also that there is no requirement for the scan planes to be evenly spaced, or event to be executed in any particular order. For example you could sample plane 1 at twice the rate as plane 2 and 3 by defining a 4-plane scan and setting z-values for the four planes accordingly.
Note: If you abort a scan at any time other than exactly at the end of a full frame, you may find that next time you run a multiplane or similar scan that the ETL and the scan mirrors are out of synch. This is because the GUI/Arduino only counts scan lines, and may thus have some remaining lines stored. To ensure this doesn’t happen, don’t update the Matlab GUI during scans. If the problem persists, simply stop the scan, and reload whatever ETL command configuration you want to execute. This will reset the counter.

XYZ scans To operate i.e XYZ mode (i.e. plane tilting), select your scan resolution (9), in the same manner for multiplane imaging (5). Select z-multiplication (10), the value of the z-shift of the last line. Z-multiplication works as follows: Say you use a 100x32 xy scan configuration in your scan mode and select a multiplication of 1. This means that for each new scan line, the ETL will be shifted by an ETL value of 1 to thus reach 32 by the last line (which corresponds to a shift of 32 in window 3). If for the same scan you will select a z-multiplication of 2, each line will be shifted by 2 to finally reach 64 by line 32 (and so on). Note that the product of the number of the number of scan lines and the multiplication factor cannot exceed 4,095.
In this way, you can also set-up a perfectly vertical scan. The simplest way might be to select a line-scan configuration in your scan software (i.e. y mirror silent). Alternatively, select an image scanning configuration and disconnect the y-mirror (just unplug it at the DAQ board - while it is not scanning!). The latter has the benefit that your scan software will display the XZ scan (as opposed to XY) as an image with Y corresponding to Z (some scan software solutions also do this for line scans so this may not be always necessary).

Note that in a “real” XZ mode (i.e. perfectly vertical), it is likely that the excitation volumes (point spread function) of subsequent z-lines will overlap because the psf is usually vertically elongated. This will give a blurred image. One way to ameliorate this effect is to slightly tilt the scan by engaging the Y mirror such that that subsequent psfs overlap less (i.e. a XYZ scan, where Y and Z are linked with the z-multiplication factor).

ETL software control: Half pipe scans
Upload ETL_HP.ino (Fig. 15) to the Arduino (instead of the “6planes” one used above). Similarly, launch the corresponding Matlab scripts GUI_HP.fig and GUI_HP.m (as above) and connect the Arduino to the GUI as before (window 1 and 2, Fig. 16).
The half-pipe GUI works in a very similar manner to the multiplane/xyz GUI.
As before, select your scan y-resolution (3). This GUI is set-up for 3 different modes (4). Standard z-shift of the entire plane (“just move”). Second, a ramp where the z-position updates linearly for each scan line up to half of the value defined under (3), and after that lineally decrease again (i.e. like a roof on a house). Third, a axial sine-wave scan. This operates like the ramp scan, except that now the z-value is updated in a sinusoidal fashion rather than linearly, which gives rise to a half-pipe-like z-scan pattern. The peak z-amplitude of these scan options is selected using slider (5) and confirmed using button (6). By definition, half-pipe and ramp scans always start from an ETL-value of zero.
ETL software control: Half pipe scans with 3 sinusoidal planes.
This mode operate on the same GUI as a standard half pike scan. Only one difference is on Arduino code. Upload ETL_HP_sin3planes.ino (Fig. 17) to the Arduino. This file is just a small modification of ETL_HP.ino described above. The difference is that third, sinusoidal scan mode operated on 3 planes imaging frame by frame. As using our ETL driver we are not able to supply negative current, now the value from slider 5 (fig. 16)

correspond to the flat, first plane, and two other planes are a sinusoidal positive half pipe with an amplitude at 2 values of slider 5, and negative sinusoidal half pipe with negative amplitude at 0.

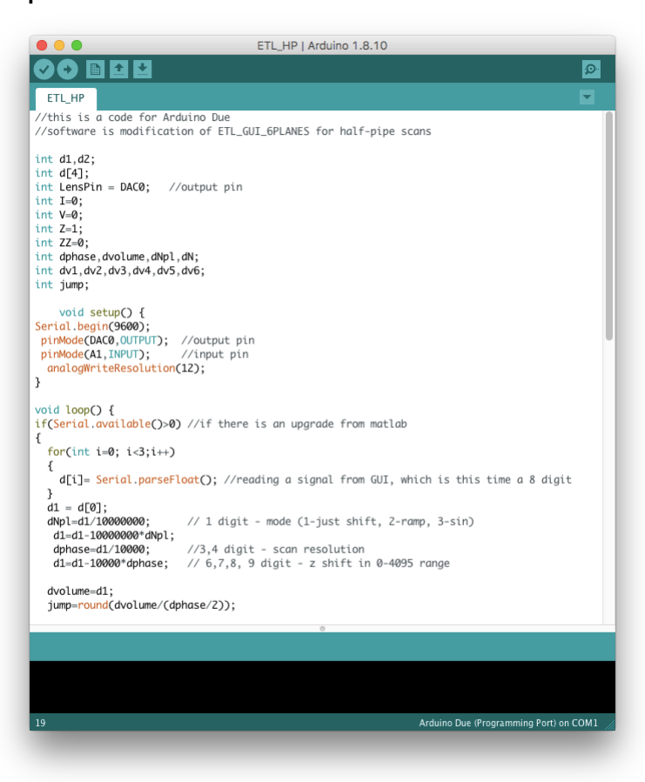
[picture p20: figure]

Fig. 15. Arduino code for Half-Pipe scans

//this is a code for Arduino Due
//software is modification of ETL_GUI_6PLANES for half-pipe scans int d1,d2;
int d[4];
int LensPin = DAC0; | //output pin
int I=0;
int V=0;
int Z=1;
int ZZ=0;
int dphase,dvolume,dNpl,dN; int dv1,dv2,dv3,dv4,dv5,dv6; int jump;
void setup() {
Serial.begin(9600);
pinMode(DAC0,OUTPUT); | //output pin
pinMode(A1,INPUT); | //input pin
analogWriteResolution(12);
}

void loop() {
if(Serial.available()>0) | //if there is an upgrade from matlab
{
for(int i=0; i<3;i++)
{
d[i]= Serial.parseFloat(); | //reading a signal from GUI, which is this time a 8 dig
}
d1 = d[0];
dNpl=d1/10000000; | // 1 digit - mode (1-just shift, 2-ramp, 3-sin)
d1=d1-10000000*dNpl;
dphase=d1/10000; | //3,4 digit - scan resolution
d1=d1-10000*dphase; | // 6,7,8, 9 digit - z shift in 0-4095 range
dvolume=d1;
jump=round(dvolume/(dphase/2));
I=0;
}
int sensVal=analogRead(A1);
switch (dNpl)
{
case 1: | // just shift
V=dvolume;
break;
case 2:{ | // ramp
if (sensVal<10){
Z=400;
}
if (sensVal+Z>1200){
Z=1;
I=I+Z;
V=I*jump;
}
if (I>=dphase/2){
V=(dphase/2)*jump-(I-(dphase/2))*jump; }
if (I==dphase){
I=0;
}
break;
}
case 3: | // sin
if (sensVal<10){
Z=400;
}
if (sensVal+Z>1200){
Z=1;
I=I+Z;
V=sin(radians(180*I/dphase))*dvolume; }
if (I==dphase){
I=0;
}
break;
}
analogWrite(LensPin,V);
}

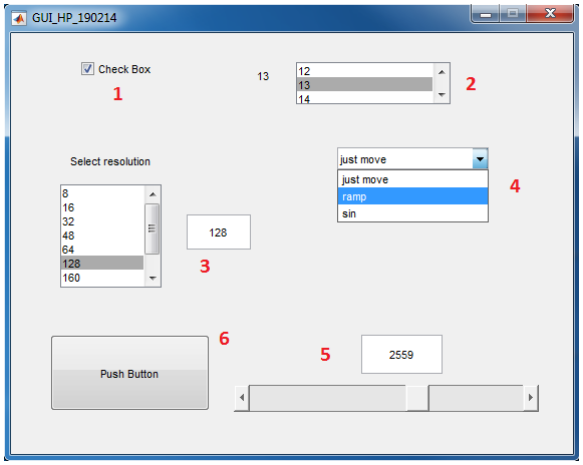
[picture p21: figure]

Fig. 16. MATLAB GUI for Half-Pipe Scans.

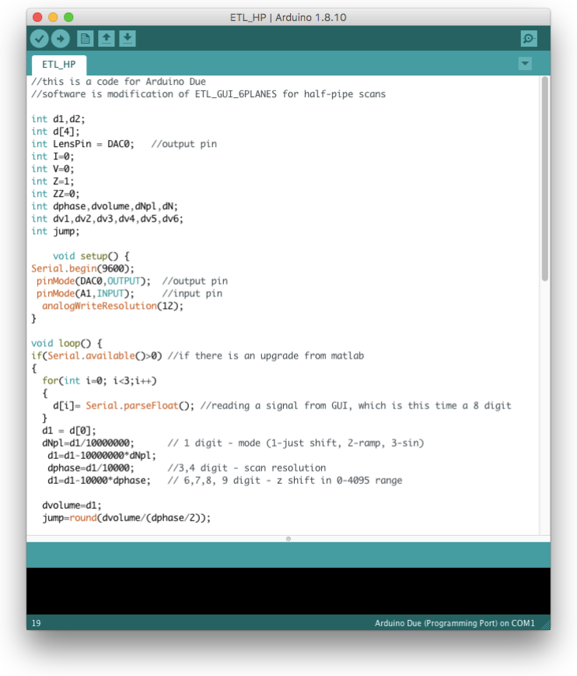
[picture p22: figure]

Fig. 17. Arduino code for Half-Pipe scans with sinusoidal 3planes imaging.

//this is a code for Arduino Due
//software is modification of ETL_GUI_6PLANES for half-pipe scans

int d1,d2;
int d[4];
int LensPin = DAC0; | //output pin
int I=0;
int V=0;
int Z=1;
int ZZ=0;
int dphase,dvolume,dNpl,dN; int dv1,dv2,dv3,dv4,dv5,dv6; int jump;

void setup() {
Serial.begin(9600);
pinMode(DAC0,OUTPUT); | //output pin
pinMode(A1,INPUT); | //input pin
analogWriteResolution(12);
}

void loop() {
if(Serial.available()>0) | //if there is an upgrade from matlab
{
for(int i=0; i<3;i++)
{
d[i]= Serial.parseFloat(); | //reading a signal from GUI, which is this time a 8 dig
}
d1 = d[0];
dNpl=d1/10000000; | // 1 digit - mode (1-just shift, 2-ramp, 3-sin)
d1=d1-10000000*dNpl;
dphase=d1/10000; | //3,4 digit - scan resolution
d1=d1-10000*dphase; | // 6,7,8, 9 digit - z shift in 0-4095 range

dvolume=d1;
jump=round(dvolume/(dphase/2));

I=0;
}

int sensVal=analogRead(A1);
switch (dNpl)
{
case 1: | // just shift
V=dvolume;
break;
case 2:{ | // ramp
if (sensVal<10){
Z=400;
}
if (sensVal+Z>1200){
Z=1;
I=I+Z;
V=I*jump;
}
if (I>=dphase/2){
V=(dphase/2)*jump-(I-(dphase/2))*jump; }
if (I==dphase){
I=0;

}
break;
}

case 3: // sin with up, down and flat (3planes) if (sensVal<10){
Z=400;
}
if (sensVal+Z>1200){
Z=1;
I=I+Z;
V=dvolume;
}
if (I>=dphase){
V=dvolume+sin(radians(180*I/dphase))*dvolume; }
if (I==dphase*3){
I=0;
}

break;
}
analogWrite(LensPin,V);
}

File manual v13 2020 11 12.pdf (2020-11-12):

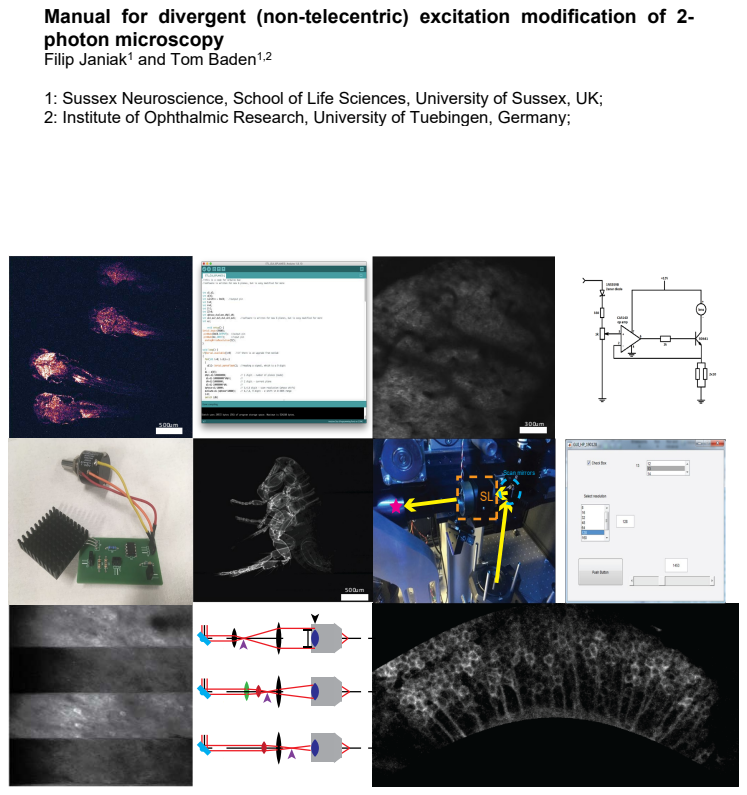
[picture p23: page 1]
Scan mirrors

Manual for divergent (non-telecentric) excitation modification of 2-
photon microscopy
Filip Janiak¹ and Tom Baden¹,2
1: Sussex Neuroscience, School of Life Sciences, University of Sussex, UK;
2: Institute of Ophthalmic Research, University of Tuebingen, Germany;

A note on safety
Remember to always wear safety googles when working with lasers! Take off all hand-worn jewellery and watches as these might reflect the beam into your or someone else’s eyes. Always work at the lowest possible laser power. And never, even with the safety glasses on, look straight into the laser beam!

What will be useful?
Tape measure, fixed fluorescence sample (i.e. a test-slide), laser viewing card

Definitions and helpful simplifications
Many of the optical elements in 2p microscopes, like the scan lens (SL), tube lens (TL) and objective (objective lens) tend to consist of multiple stacked lenses with different curvatures and thickness. For simplicity, we treat each of these as a single ideal lens.

In detail: There is a large set of parameters describing optical properties of such lenses, however for us important are only the following: principal planes (P, P’), focal planes (F, F’), surface vertices (V, V’), and three focal lengths: effective focal length (EFL), back focal length (BFL) and front focal length (FFL). For details on any of these, see also the following Wiki articles:
https://en.wikipedia.org/wiki/Cardinal_point_(optics) https://en.wikipedia.org/wiki/Focal_length

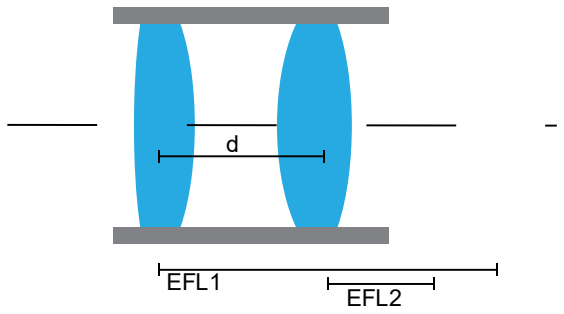
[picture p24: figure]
EFL1; EFL2
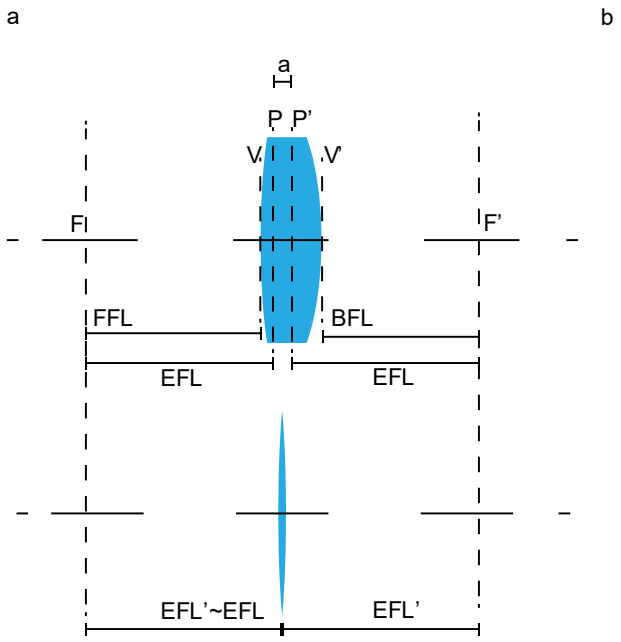
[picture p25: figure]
FFL; BFL; EFL; EFL’~EFL; EFL’
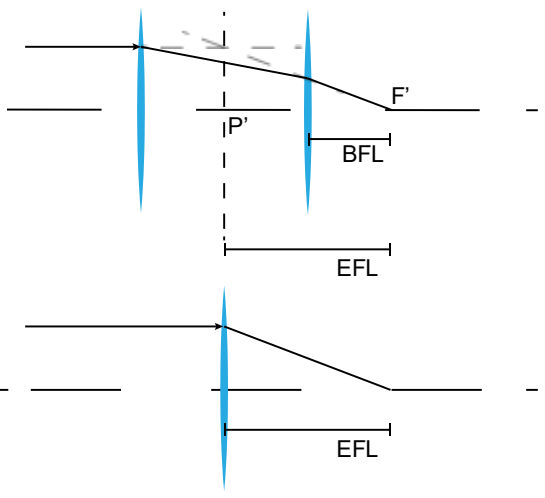
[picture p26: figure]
EFL; BFL

Fig 1. Thin lens approximation of a thick lens (a). Single thin lens approximation of two thick lenses (b).

In optical models, such constituent lenses can be replaced by a single, thin, ideal lens, and for simplicity this is what we are doing in all calculations and diagrams. This ideal lens has a negligible thickness, so principal points are located exactly in a centre of the lens, and effective, back and focal length are the same, and equal to EFL of thick lenses corrected by half of the thickness (EFL’ on fig 1). Typically, the thickness can be disregared if EFL>> thickness.

# EEEELL′ = EEEE +

aa

# 2 iiii (EEEE ≫ aa) EEEELL′ ≅ EEEE

To calculate effective focal length of two thin lenses, we can use:
1

# EEEE = 1

## EEEE 1

+

1

## EEEE 2

− dd

# (EEEE 1)(EEEE 2)

Or just simply:

1 = 1
1

+

1
2

− dd
1 2

See more on https://physics.stackexchange.com/questions/247617/how-is-focal-length-defined-for-a-two-lens-system-separated-by-a-distance-d (https://physics.stackexchange.com/questions/247617/how-is-focal-length-defined-for-a-two-lens-system-separated-by-a-distance-d)
This ideal lens is located in the back principal planes of complex lenses (which is usually in the centre of a given tube).

Initial steps: Obtaining all the key numbers of your specific setup.

This section is intended to help identify all key elements in your laser path between the scan mirrors and the sample plane, and to obtain concrete values for their relative distances and focal lengths etc..
1. Identify scan lens (SL). It should be the first lens ensemble after the scanning mirrors (from point of view of the laser source). Identify Tube Lens (TL), it should be the next one after SL. Measure the distance between them (D2).
2. If focal lengths and dimensions are unknown, carefully take out both lenses. Use gloves to avoid leaving smear-marks, and do not scratch them. Measure their focal distance (FSL,FTL), and their dimensions (ØSL, ØTL), for example as demonstrated here:

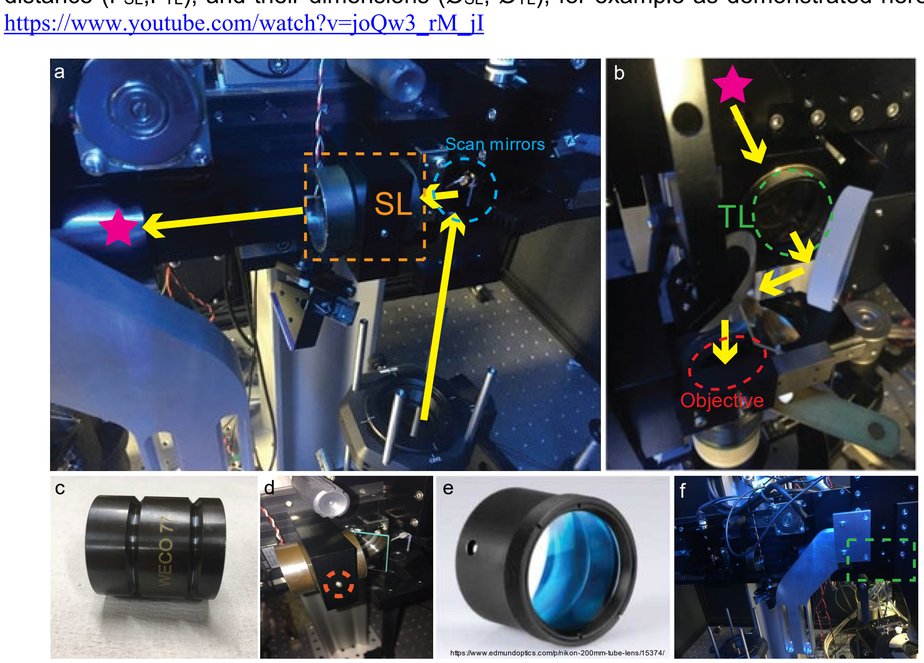
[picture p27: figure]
https://www.youtube.com/watch?v=joQw3_rM_jI; https://www.edmundoptics.com/p/nikon-200mm-tube-lens/15374/; Scan mirrors; Objective

Fig 2. Sutter MOM setup with DL standard configuration. Location of SL (a), TL and objective (b). SL outlook (c) and mounting (d). TL outlook (e) and position from the side (f).
If you use a Sutter MOM setup, the SL model is VISIR 1534SPR136 from Leica (Fig. 2a), which is mounted in a WECO 77 tube (Fig. 2c). It has a focal length of 50 mm, and it is located 56.6 mm from second scan mirror. The thickness of the lens (which is made up of two biconvex lenses) is 43.1 mm. The external tube diameter is 38.2 mm, and the internal aperture diameter is 28.9 mm. It is easy to unscrew and take out (Fig. 2d). However, in the Sutter MOM the TL (MXA22018, Nikon) is less readily accessible (Figs. 2b,f). It has a 200 mm focal length (Fig. 2e) and is positioned at a distance of 250 mm from the SL. The length of the TL tube is 29 mm, and it has a 36 mm aperture.
3. For your objective, check the magnification, nominal working distance, and size of the back aperture (Øobj). Measure the total distance between the objective’s back aperture and the SL.

Note: Microscope objectives are designed to correct for chromatic aberration at a specific distance D3 between TL and its back aperture OBA. For Zeiss objectives, D3 = 95 mm. (Philbert S. Tsai and David Kleinfeld, 2009).
In our setup, we use a Zeiss Objective W "Plan-Apochromat" 20x/1.0, 1.8 mm working distance.
In a standard diffraction limited (DL) configuration, the distance between SL and TL is equal to the sum of their focal distances D2=FSL+FTL. D3 is specified by the objective as discussed above.
4. Based on these numbers, calculate the distance D1 between the second scan mirror pivot point and SL that minimizes motion of laser beam (intensity fluctuation) on

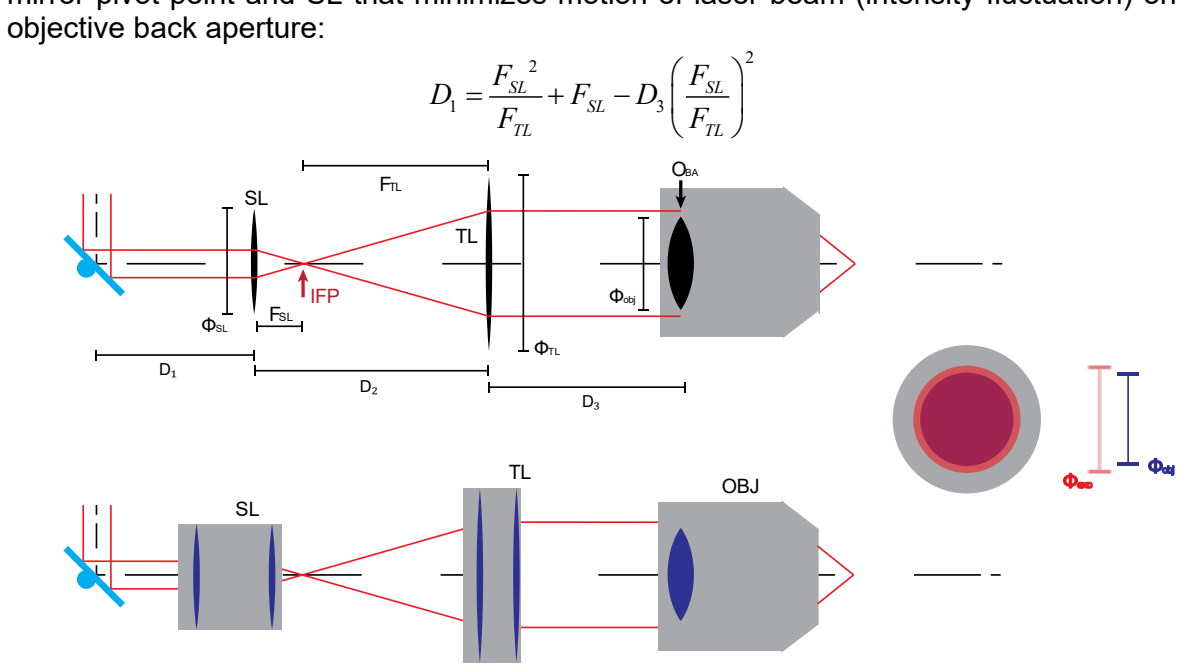
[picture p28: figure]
objective back aperture:; FSL; FTL; ФSL; ФTL; Фobj; OBA; IFP; OBJ

Figure 3. DL configuration. Ideal lenses approximation (top), objective back aperture overfilling (left) and typical configuration with stacked lenses (down).

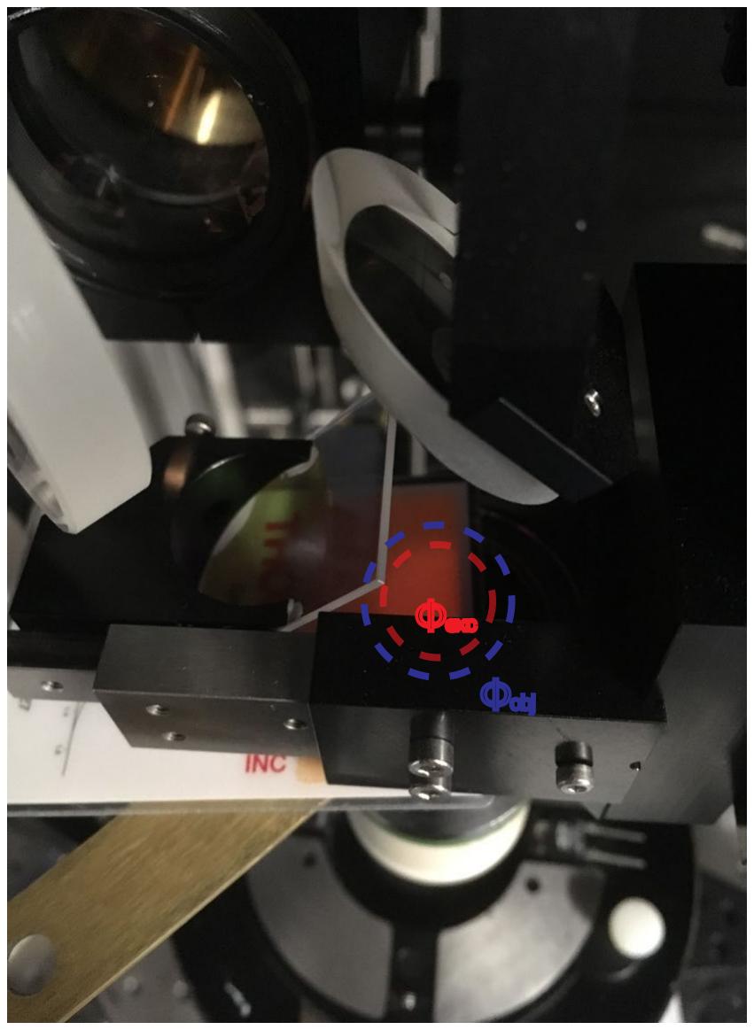
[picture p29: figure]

5. Check objective’s back aperture (OBA) filling factor (Øexc/Øobj). To do so, turn on a regular scan mode at “high zoom” (i.e. with minimal movement of scan mirrors) without the objective in place. Use a laser viewing card in the position where the objective’s back aperture would be to assess the setup’s fill factor (i.e. the size of the laser spot relative to the objective’s back aperture) (Fig. 3, 4). Alternatively, if your laser supports an alignment mode at a visible wavelength (typically low 700s of nm) you can also do this procedure with a piece of paper in place of the laser viewing card.
In a DL configuration, overfilling OBA by the excitation laser beam minimizes the lateral and axial size of the excitation spot (point spread function, psf), but also decreases effective excitation power delivered by the objective (Helmchen & Denk, 2005; Philbert S. Tsai and David Kleinfeld, 2009).

This manual describes how to change a setup from a DL configuration. Therefore, based on your data, check and calculate if your setup operates on DL settings.
If it is, go ahead to the next section. If it is not, try to understand why. There are two main possibilities. First, unintentional misalignment during a construction/mainlining or a using of the setup, which can be easily fixed to come back to DL configuration or apply a modification. Second, intentional changes from DL configuration. In this case you need to check why your setup is designed in this specific manner (e.g. if there are specific advantages/limitations). In this case, application of our modifications could be more complicated, but may still be possible.

We present two modifications to obtain a divergent excitation 2-photon setup leading to an expanded field of view (FOV) and excitation spot (point spread function, psf).
Throughout, we will be focussing on two parameters: Intermediary focal point (IFP) and the objective’s back-filling factor (Fig. 5):
Intermediary focal point (IFP) position | Objective back aperture filling factor


Fig. 5. IPF positions (left) and objective back aperture filling factor (right) for 3 configurations DL(a), nTC1(b) and nTC 2(c).

## nTC1 configuration

1. For “non-telecentric modification 1” (nTC1), the goal is to move the IFP closer to the TL, yet without passing it, while simultaneously underfilling OBA (Fig. 6).
2. To assess the extent of any changes, use a fixed fluorescence sample. Prepare your setup for a standard experiment with DL configuration. Using lowest possible power find a suitable sample plane (one with obvious structure) and determine the original maximal FOV and working and working distance (e.g. by moving the sample side to side and checking when a particular image structure leaves the field of view).
3. Prepare setup to measure objective back aperture (OBA) filling factor (Øexc/Øobj) – see initial steps.
4. Completely remove SL from the system. Before implementing any modifications, remember to switch off the laser!


Sidenote: Why not simply shift the original SL? We can of course move the IPF closer to TL by simply shifting forward the SL. However, this will increase overfilling OBA (we are hoping to decrease this) which in turn will decrease effective excitation power on the sample plane (we are hoping to increase this).
Fig 6. Optical design of DL(a) and nTC1 configuration (b-d). Left part shows positions of the lens, right objective back aperture filling factor. (b and c) shows different positions on

L2 and in result different FOV and psf shape. (d) shows configuration (b) without thin lens approximation.
5. Insert new lenses in place of the SL. In our tested nTC1 solution for the Sutter MOM, we use 2 lenses in place of the SL: L1 and L2, with focal lengths 190 and 175 mm, respectively.

In our implementation, L1 is a modified Sutter MOM SL - VISIR 1534SPR136, Leica (Fig. 7b), and L2 is LA1229 from Thorlabs (Fig. 7c). This specific choice for L1 is one of convenience, but it can be equally be replaced by a new 190 mm lens.
nTC1 can also be achieved using a single lens. However, in this case, the OBA filling factor will be much smaller and difficult to control, and the psf will disproportionately inflate already for a small FOV increase.
For mounting L1, we use the original SL mount (as our L1 is a modified SL). For assembling and shifting L2, we use a 3D printed lens holder that fits into the existing tube that also holds the TL at its end (Fig. 6a). The 3D printable file Lens_holder.stl is found on our GitHub.

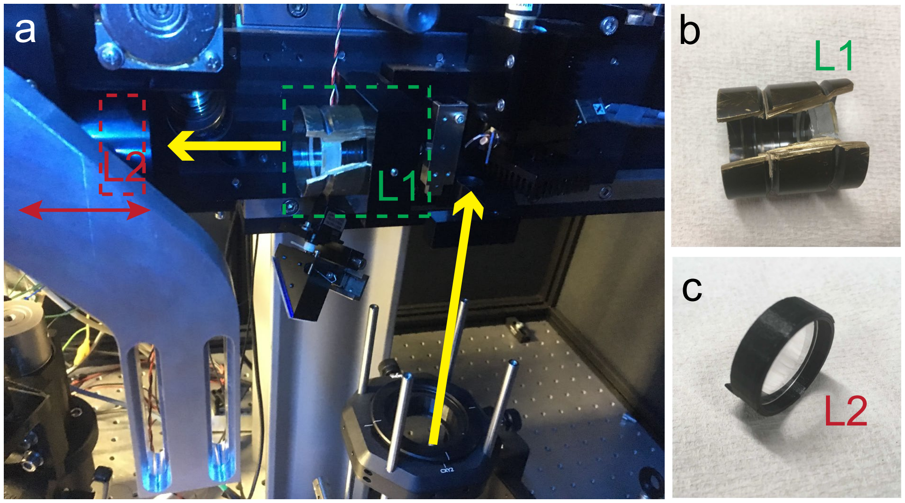
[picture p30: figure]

Fig 7. Sutter MOM setup with nTC1 configuration. Location of L1 and L2 (a), L1 modified from Leica VISIR 1534SPR136 (b), L2 with custom design 3D printed holder (c)
6. Select the “right” L1 and L2 lenses for your setup.
Sketch out how you want the optical configuration of your setup to look like. Note original SL, TL and their apertures. Note existing holders for lenses and the physical constraints imposed by your setup’s mechanics to position and shift L2.

For L1, use a lens with a focal distance FL1 = DL1, such that by itself, L1 sets up an IFP exactly at the centre of the TL. We use a 190 mm lens, positioned 190 mm in front of the TL.

If desired, you can also use an L1 with shorter or longer focal distance than DL1. However, if the focal distance is shorter, the range of FOV changes generated by shifting of L2 position decreases. In contrast, of L1 focal distance is longer than DL1, it will bring the IFP behind the TL, effectively resulting in nTC2 (discussed below). In this case we can shift between modification 1 and 2 mode by change a position of L2.
Make sure that the aperture (diameter) of L1 is suitable. It should be in similar range as the original SL (ØL1 ≈ ØSL) to make sure the incoming laser beam does not get clipped on the edges during scanning.
For L2, the focal length (FL2) should be in the range between FL1 and FL1/2. FL2 shortening introduce an overfilling of OBA, or even TL aperture, resulting in power lost and fluctuation of excitation intensity on FOV. FL2 extending decrease range of IFP and (Øexc/Øobj) changes.

On our setup, we use a 175 mm FL2, which is shifted along the laser path between 100 and 5 mm from TL.
Ultimately, the exact position vale of FL2 as well as the position of L2 relative to L1 and TL will dictate the position of the IFP, and thereby set the (Øexc/Øobj) factor, FOV and the size of the excitation psf.
If possible, choose an aperture of L2 that is similar to the one for L1 (ØL1 ≈ ØL2). In our case it was not possible to use the exact same size, so we used the largest possible L2 diameter (25,5 mm) which just about fit into the 3D printed holder that was slotted into the tube that also held the TL.
7. Test the result of your changes and establish the range of FOV shifts achievable by shifting L2 up and down the laser path. Start by setting L2 as close as it is possible to L1 and take a scan of your fixed sample. Likely, working distance will be longer than in the original DL configuration so you will need to refocus. Note the difference of a working distance and check the maximal FOV size. Also, zoom in to assess spatial resolution. Now, shift L2 closer to TL and again check FOV and working distance. Both should increase. Note the range of changes that can be achieved with this configuration. Remember to shift L2 only when you are not scanning and your laser is disabled!

If you find that working distance and FOV starts to decrease again at some point when shifting L2 closer to TL, it means that L2 is further away from L1 compared to L1’s focal distance. In this case, put L1 closer to TL or exchange it for the one with longer working distance.

8. As for 7, also check the objective filling factor (Øexc/Øobj) for a different positions of L2 (see initial steps paragraph). Shifting of L2 towards TL will increase underfilling (i.e. will make the laser spot smaller at the level of the objective’s back aperture), and should result in an expansion of the psf.

If desired, you can try to keep a (Øexc/Øobj) constant even with increasing FOV by exchanging of L2 for one with shorter working distance as you shift it closer to TL. This effectively allows setting FOV somewhat independently of psf expansion (up to a point). Sidenote: Remember that overfilling of OBA will reduce effective excitation power, and can also lead to uneven excitation power across the FOV.
9. As desired, you can also directly measure the excitation psf, for example by imaging fluorescent beads embedded in agarose. When doing so, remember to keep laser wavelength and excitation power at the sample plane approximately constant to ensure fair comparison (measured psf dimensions strongly depend on these factors). Note that excitation power at the sample plane should also increase as you decrease Øexc/Øobj, so it is best to directly measure this on the sample plane using a power meter.

## nTC2 configuration

1. In nTC2, goal is to move the IFP beyond the TL (but still in front of OBA), again while ensuring underfilling of OBA (Fig. 7). Most steps to set-up nTC2 are very similar to those required to set up nTC1. Therefore, first consult the description in nTC1. From here, implementation nTC2 will be straightforward:
2. Starting from a nTC1 configuration, remove L1 from the setup and replace L2 with L3. (If you start from a DL setup, simply remove the SL entirely, and find a way to mount L2/L3 in front of the TL).

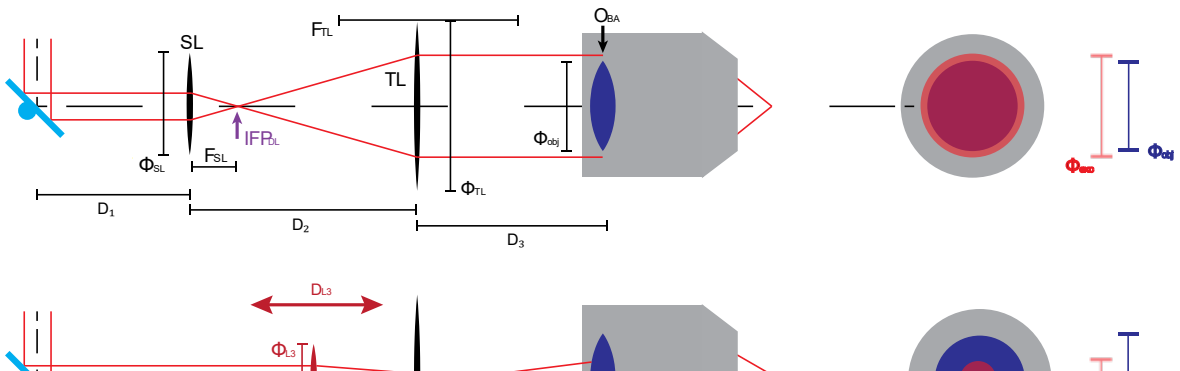
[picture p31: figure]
FSL; FTL; ФSL; ФTL; Фobj; OBA; IFPDL

Fig 8. Optical design of DL(top) and versions of nTC2 configurations (below). Left: positions of the lens(es), right: objective back aperture filling factor. Different positions of L3 and in result different FOV and psf shape. Bottom row shows configuration without thin lens approximation (see introductory definitions). To compare with nTC1 check Fig 6.

3. How to select L3? The goal of L3, depending on its position in front of TL, is to shift the IFP anywhere between the TL and OBA. In our setup we use a 200 mm focal length Ø1 plano convex lens (LA1708, Thorlabs) which is probably a good starting point for most optical configurations. L3 is assembled exactly like L2 in nTC1, using a 3D-printed holder. In our configuration we can slide it anywhere between just next to the TL and up to 10 cm in front of it.

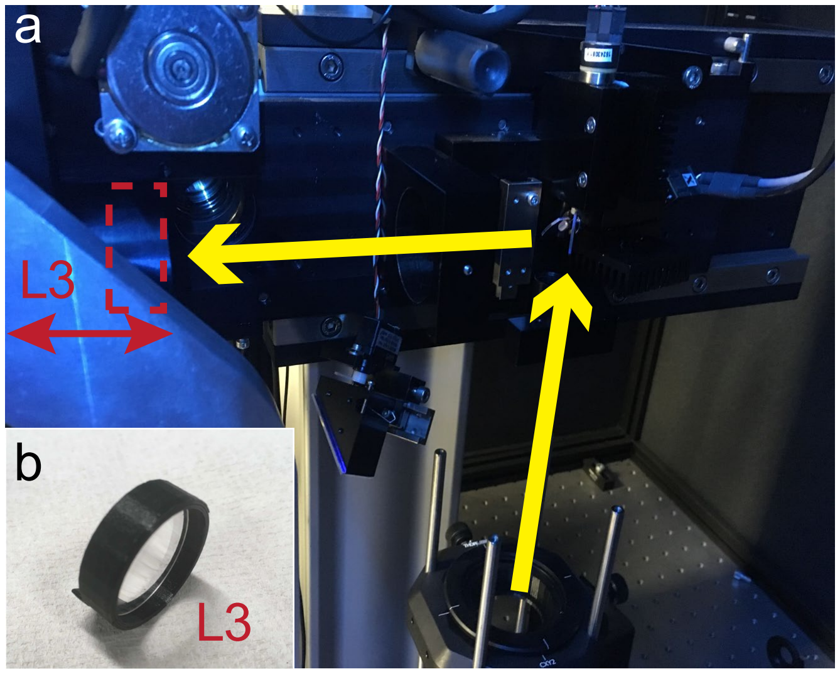
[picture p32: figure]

Fig. 9. Sutter MOM setup with nTC2 configuration. Location of L3 (a) and L3 with custom design 3D printed holder (c)
Side note: If you remove all lenses except the TL and Objective (i.e. remove SL/L1/L2⁽*)), your parallel beam coming from the scan mirrors should come into focus beyond the objective back aperture (FTL is always bigger than D3). Accordingly, OBA will be illuminated by convergent beam. However, we want the beam to diverge, so you will need a L3 lens that is powerful enough to generate an IFP (just) before the laser beam reaches the objective.
Check always that the beam reaching the OBA is divergent, not convergent (for example with a laser viewing card).
Throughout, when choosing new lenses, make sure they have high transmission efficiency in the infrared range such that the laser beam does not get attenuated too much.
Remember to use the highest possible aperture of the lens. Of course, this factor will be limited by space in Your scope (in our cases size of the tube where L3 is moved. Selection of a too small aperture will likely result in inefficient collection of the excitation beam after the mirrors (as now there is no longer a SL to direct the beam onto L3).

Electrically Tunable Lens
In our setup we implemented an Electricaly Tunable Lens (ETL) for rapid axial focussing. Our ETL is an EL-16-40-TC20D, Optotune, controlled by a custom driver and custom written software (see GitHub).
ETL Optics

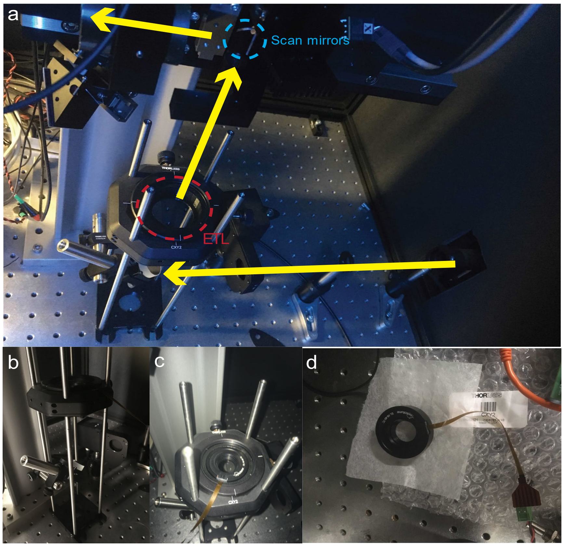
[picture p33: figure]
Scan mirrors; ETL

Fig 10. Sutter MOM setup with cage for ETL (a). View of the cage with ETL holder, and mirror reflecting excitation beam to scan mirrors (b), ETL on the holder (c) and ETL EL-16-40-TC20D by itself (d).
In our approach, we decided to use an ETL which operate in a range of -10 to +10 dpt. This means that it focuses from infinity (∞, no focus, parallel beam) to -10 cm for negative current and from ∞ to +10 cm for positive current. If the ETL is not supplied by any current, it does not strongly interfere light which is going through (according to the product manual, it introduces a negligible, long range focus).

The main idea is to locate the ETL far away from the objective (compare to original idea presented by Grewe (Grewe, Voigt, van ’t Hoff, & Helmchen, 2011)). By changing the ETL’s focus from infinity to a positive value (supply positive current) we can then introduce a small convergence into the excitation beam before it hits the scan mirrors. This effectively elevates the imaging plane under the objective. In our solution, we are operating around 25% of a maximum ETL power, which give us an effective focus shift of up to 600 µm.
On our setup, the ETL in mounted horizontally on custom cage build from Thorlabs elements (more details in bill of materials, BOM). Fig. 10a presents the layout of the ETL holder on our Sutter MOM setup. We replaced the Sutter MOM-s original tube with mirror (which bounces the excitation beam from below onto the scan mirrors) by our cage including a new mirror. This new mirror can be adjusted in xyz directions, and in reflection angles, to help setup a perfectly vertical beam. The ETL holder is adjustable in x and y, and is located 20 cm below the first scan mirror.

ETL driver hardware

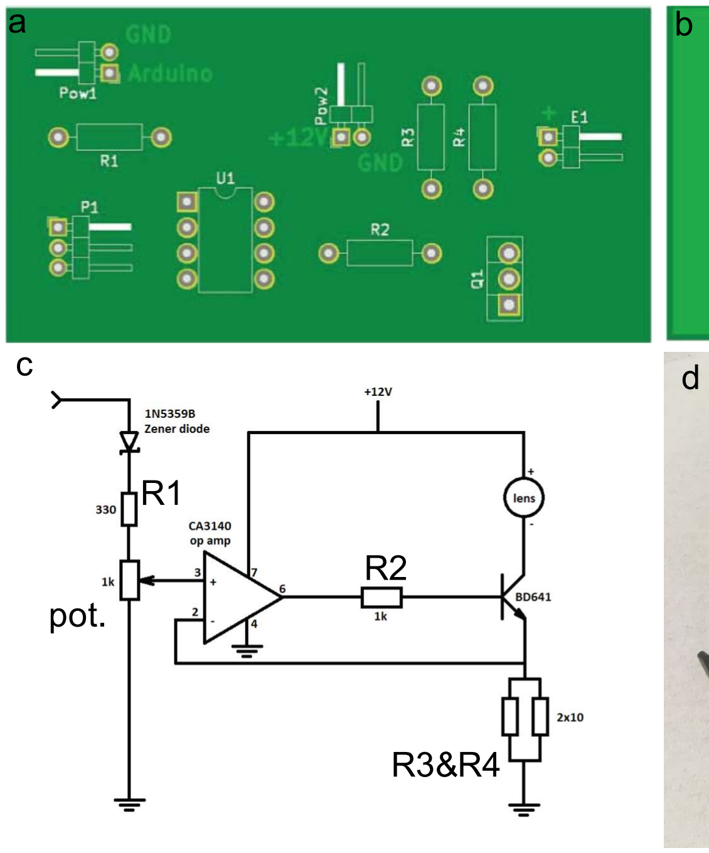
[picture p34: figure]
pot.
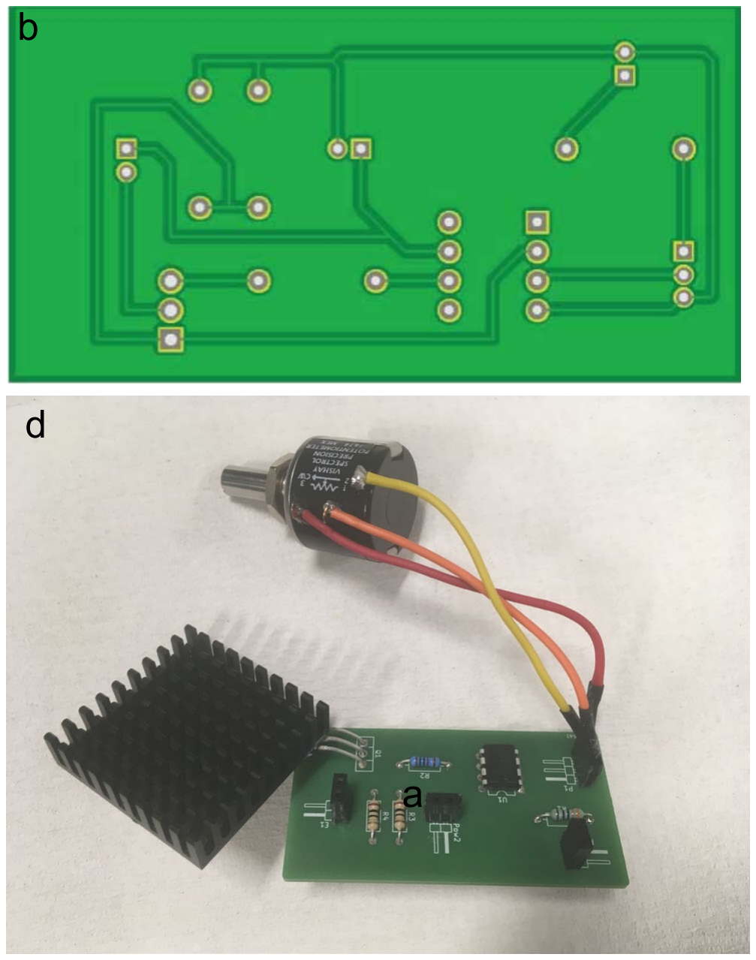
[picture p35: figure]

Fig 11. Top (a) and bottom (b) view of ETL driver printed circuit board (PCB). Schematic of electrical circuit (b) and photograph of the assembled driver (d). The Gerber files for producing the PCB are available on the project GitHub.

To control our ETL, we are using a custom designed current driver combined with an Arduino Due microcontroller. The driver’s overall goal is to generate ETL command signals that are line-synchronised with the 2-photon scan engine. For this, the Arduino Due reads a line-signal from the scan engine (e.g. a copy of the fast-mirror command, or a line-synchronised TTL pulse) to count lines. For this, the Arduino is reading such as signal on Analog pin A1. In our case, this signal is simply a copy of the “banking signal” which we send to the Pockels Cell during the scan retrace (the latter is an optional “trick” to reduce bleaching during retrace times, this has been discussed previously e.g. in Euler et al. 2009 Pflueger’s Archive).
Upon reading this signal, the Arduino “counts scan lines”, and executes driver commands accordingly, based on a custom script controlled from a Matlab GUI (below). For this, the Arduino sends a driving signal through its Digital-Analog-Converter (DAC) output port into the custom driver board. On the Arduino side, this DAC signal is ranges from 0 to 4,095 (12 bit), which corresponds to a voltage range of 0.55 - 2.75 V, which serves as the sole scan input to the custom driver board. First, the 0.55 V offset (corresponding to 0 on the Arduino) is removed using an operational amplifier (op-amp). Next, the remaining signal is scaled using a potentiometer which allows defining the maximum current sent to the ET (which also indirectly defines its resolution). Finally, this signal is used to open a negative-positive-negative (NPN)-transistor, which works as a switch for a current from a separate +12V 0.42 A power supply.

Note that our current driver works only for a positive current, even if our ETL works also for the negative.
Note that we are using an additional Zener diode as a connector between Arduino output and our current driver input. Reason of using it was additional protection of current driver and ETL because of problems with series of unstable Arduino boards which we have been using (some of them temporary didn’t work properly). This Zener diode introduce additional voltage drop to the system, so it doesn’t need to be done on op-amp.
Figure 11a and b shows the PCB of our driver. PCB file ETL_driver_board.kicad_pcb is available for download on our GitHub. In addition, you will need the following electronic components (full details on BOM):
- Zener diode (1N5359B) (additional used as connector between Arduino and driver board – see note above),
- R1 330 Ω,
- 1kΩ potentiometer,
- Op-amp CA3140EZ,
- R2 1 kΩ,
- R3&R4 10 Ω.
- N6039G transistor
- 12 V 420 mA power supply.

All connection pins are labelled on the board (Arduino, +12, + (ETL), and GND for Arduino and power supply). The Pin next to + is a negative connection for ETL.

Note that in addition we attached a heat sink to the N6039G transistor which helps to dissipate heat if the driver is operated for prolonged periods of time (see photo in Fig. 11d).

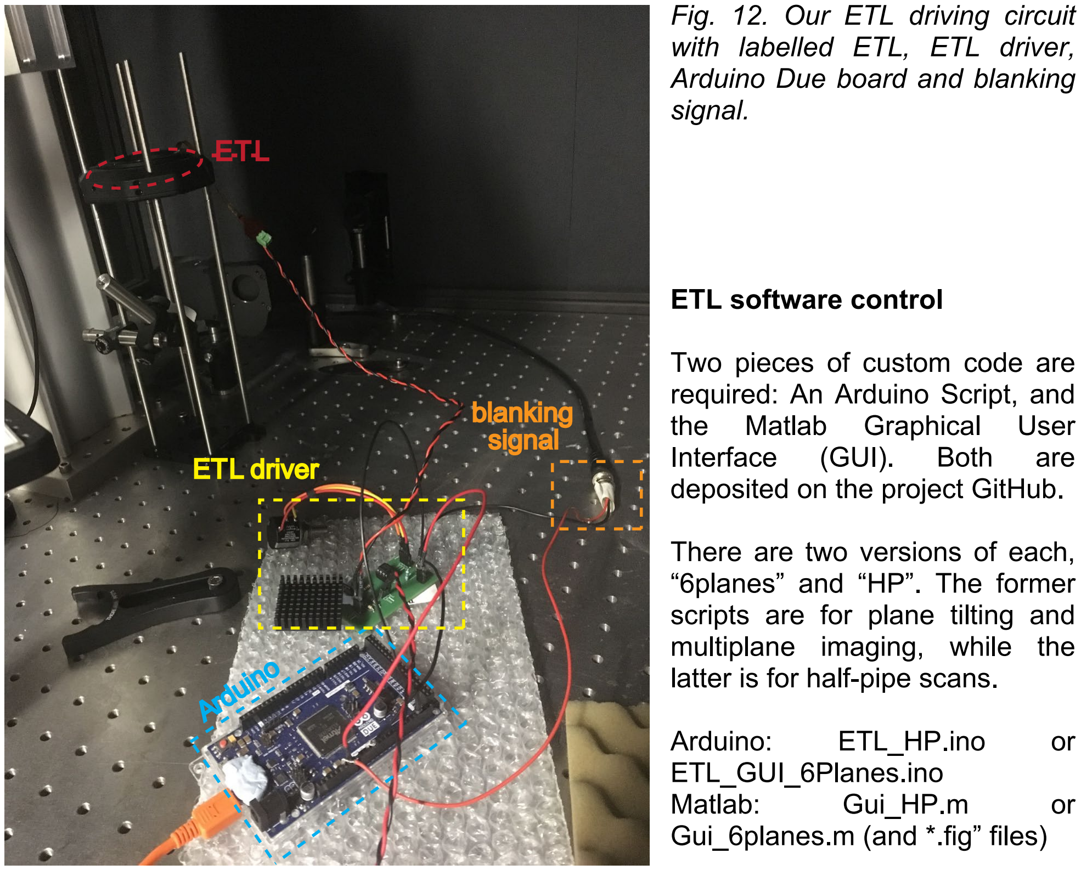
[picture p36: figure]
Fig. 12. Our ETL driving circuit with labelled ETL, ETL driver, Arduino Due board and blanking signal.; ETL software control; Two pieces of custom code are required: An Arduino Script, and the Matlab Graphical User Interface (GUI). Both are deposited on the project GitHub.; There are two versions of each, “6planes” and “HP”. The former scripts are for plane tilting and multiplane imaging, while the latter is for half-pipe scans.; Arduino:; ETL_HP.ino; ETL_GUI_6Planes.ino; Matlab:; Gui_HP.m; Gui_6planes.m (and *.fig” files)

Our software control is fully independent from the software used to control the 2P microscope (e.g. ScanImage, or in our case ScanM), meaning that it can in principle be seamlessly integrated with any working 2p system so long as a line-synch signal is available to be read by the Arduino.
To communicate with the Arduino and upload the script, download the Arduino integrated development environment (IDE). The Arduino IDE is freely available at https://www.arduino.cc/en/main/software. Tutorials on how to connect the Arduino via serial link and upload scripts are widely available online, so we will not cover this step here. You only have to upload the script once (the Arduino stores it locally), but you will need to keep the Arduino connected to your computer prior to changing any scan configuration so as to allow the Matlab script to communicate with it (see below).
Our GUI is written in MATLAB (Mathworks), which is widely using in academia. If you do not have it on your computer, check if your institution has a licence for it. There is also a 30-day free trial version https://uk.mathworks.com/products/matlab.html.

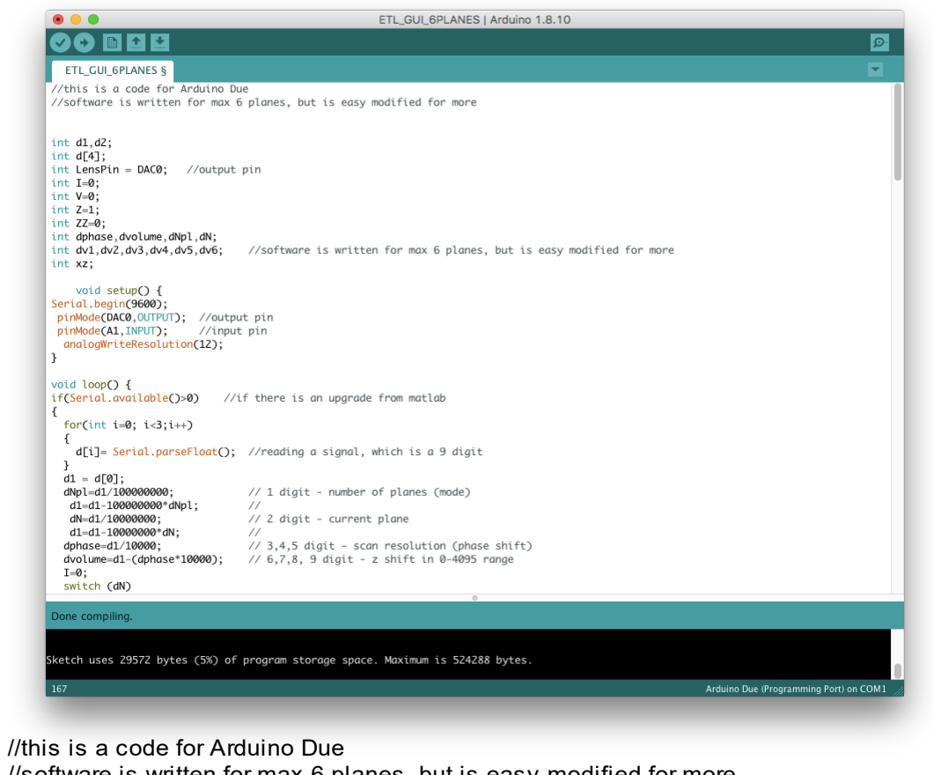
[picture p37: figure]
//this is a code for Arduino Due

//software is written for max 6 planes, but is easy modified for more

int d1,d2;
int d[4];
int LensPin = DAC0; //output pin
int I=0;
int V=0;
int Z=1;
int ZZ=0;
int dphase,dvolume,dNpl,dN;
int dv1,dv2,dv3,dv4,dv5,dv6; //software is written for max 6 planes, but is easy modified for more
int xz;

void setup() {
Serial.begin(9600);
pinMode(DAC0,OUTPUT); //output pin pinMode(A1,INPUT); //input pin analogWriteResolution(12);
}

void loop() {
if(Serial.available()>0) //if there is an upgrade from matlab {
for(int i=0; i<3;i++)
{
d[i]= Serial.parseFloat(); //reading a signal, which is a 9 digit }
d1 = d[0];
dNpl=d1/100000000; // 1 digit - number of planes (mode) d1=d1-100000000*dNpl; //
dN=d1/10000000; // 2 digit - current plane
d1=d1-10000000*dN; //
dphase=d1/10000; // 3,4,5 digit - scan resolution (phase shift) dvolume=d1-(dphase*10000); // 6,7,8, 9 digit - z shift in 0-4095 range I=0;
switch (dN)
{case 1:
dv1=dvolume;
case 2:
dv2=dvolume;
case 3:
dv3=dvolume;
case 4:
dv4=dvolume;
case 5:
dv5=dvolume;
case 6:
dv6=dvolume;}
}
int sensVal=analogRead(A1); //reading blanking signal switch (dNpl)
{
case 1: //for xyz scans

if (sensVal+Z>1200){ // 1200 is a average noise value read from A1. PLEASE CHECK IF IT
IS | //CORRECT FOR YOUR SETUP
int xz=round(3*4095/dphase);
Z=1;
I=I+1;
}
V=I*dvolume;// z shift for xyz

if (I==dphase){
I=0;
}

case 2: // 2 planes

if (sensVal<10){
Z=200; //2Z=200 is a treshold value betwen HI and LOW of blanking signal for our setup. //PLEASE CHECK IF IT IS CORRECT FOR YOUR SETUP
}
if (sensVal+Z>1200){
Z=1;
I=I+Z;
}
if (I==dphase){ //change z volume no 1 V=dv1;
}
if (I==dphase*2){ //change z volume no 2 I=0;
V=dv2;
}
break;
case 3: | // 3 planes
if (sensVal<10){
Z=200;
}
if (sensVal+Z>1200){
Z=1;
I=I+Z;
}
if (I==dphase){
V=dv1;
}
if (I==dphase*2){

V=dv2;
}
if (I==dphase*3){
I=0;
V=dv3;
}
break;
case 4: // 4 planes
if (sensVal<10){
Z=200;
}
if (sensVal+Z>1200){
Z=1;
I=I+Z;
}
if (I==dphase){
V=dv1;
}
if (I==dphase*2){

V=dv2;
}
if (I==dphase*3){

V=dv3;
}
if (I==dphase*4) {

V=dv4;
I=0;
}
break;

case 5: // 5 planes
if (sensVal<10){
Z=200;
}
if (sensVal+Z>1200){
Z=1;
I=I+Z;
}
if (I==dphase){
V=dv1;
}
if (I==dphase*2){

V=dv2;
}
if (I==dphase*3){

V=dv3;
}
if (I==dphase*4) {

V=dv4;
}
if (I==dphase*5){
I=0;
V=dv5;
}
break;

case 6: // 6 planes
if (sensVal<10){
Z=200;
}
if (sensVal+Z>1200){
Z=1;
I=I+Z;

Fig 13. Arduino code with comments for multiplane and xyz imaging.

ETL software control: Multiplane and XYZ imaging
First, upload the Arduino script ETL_GUI_6Planes.ino (called a “Sketch” in Arduino) to the Arduino board. Once this is done, you can close the Arduino IDE.
Next, open MATLAB and launch Gui_6PLANES.fig and Gui_6PLANES.m (If you are unsure how to do this, look for an online tutorial how to launch code in MATLAB.). In short, put both files into a common folder, change the MATLAB path to this folder, and execute Gui_6PLANES.m. This should bring up the GUI (Fig. 14).
From within the MATLAB GUI, connect the Arduino. For this, select the serial (COM)-port to which the Arduino is connected (Fig. 14, list 1) (It will be the same that you previously used to upload the Arduino script - if you are unsure how to identify the Arduino’s COM-port, search for one of the many tutorials online). In our cases it happens to be COM 13. Note: ensure that the COM port is not busy – this can easily happen if the Arduino IDE’s serial monitor happens to the open, or if it is still uploading the script.
Next tick the “ETL ON” checkbox to connect to the ETL. This sets up an open serial communication between Matlab and the Arduino (this also means that you can no longer communicate with the Arduino from elsewhere, e.g. the Arduino IDE. So, if you want to upload e.g. a different Arduino script, you need to untick the ETL ON box again).
From here, you are ready to start using the ETL in synch with the scan commands. Remember, in our implementation, the ETL can only lift the imaging plane, so the lowest position of your desired scan should be defined by the actual objective position (ETL at position 0)
Search-z function. To statically change the z-plane of your scan, simply enter a value between 0-4,095 into window (3) and press button (4) to confirm. Each time you do this the GUI sends a command to the Arduino, which in turn will send a static driver signal to the ETL and thus shift the imaging plane. This function is useful to explore by hand which values entered into the GUI correspond to what kind of actual z-shift. Confirm that this works by running any xy-scan on your scan software and changing this number (you don’t need to stop the scan for this). It may take a few seconds for any change to take effect.

case 6: // 6 planes
if (sensVal<10){
Z=200;
}
if (sensVal+Z>1200){
Z=1;
I=I+Z;
}
if (I==dphase){
V=dv1;
}
if (I==dphase*2){

V=dv2;
}
if (I==dphase*3){

V=dv3;
}

if (I==dphase*4) {

V=dv4;
}
if (I==dphase*5){

V=dv5;
}
if (I==dphase*6) {
I=0;
V=dv6;
}
break;
case 7: // single plane shift for z seachhing V=dvolume;
break;
}
analogWrite(LensPin,V); //write value to current driver }


Fig 14. MATLAB GUI for the multiplane and xyz imaging.
Z-shift calibration (optional). Use a structured fluorescence sample (e.g. a test-slide) that allows you to easily identify specific structures at different imaging depths. Prepare your setup for standard 2P imaging, find a suitable image plane without engaging the ETL (ETL disconnected or set to “0”). Now, put the maximum allowed value of 4,095 into window (3), and push button (4). This should jump the imaging plane upwards, and potentially quite substantially so (in our case some 600 microns). Now go down in your sample using the objective and find the same imaging plane again. Take a note of the effective note the z-shift that you needed to use to compensate for the ETL. This is the maximum z-jump range possible with your configured optics and ETL-driver settings as defined by the potentionmeter (see driver). If this range is too small or too large for your purposes, rotate the potentiometer by a few turns and repeat the above. Once you are happy with the effective z-jump range, ensure that the dependency between the number entered into the GUI and the effective z-jump is approximately linear (it is very linear in our case, where we use ~25 max driving current on the ETL).
Scan-synchronised ETL commands. For any of the above procedures, the line-counting feature of our custom driver is not really used as the driver is just outputting static commands. However, for multiplane imaging, tilting the scan plane (xyz scans) or for halfpipe scans (see next chapter), the ETL must be synchronised to the scan mirrors with the line-synch connection (see driver chapter above).
Multiplane and staircase scans. Here, the control logic of our GUI is simple – for multiplane imaging it simply jumps the ETL to a new current (and hence effective focus position) once it counts a certain number of scan lines based on the values you enter under “select y resolution” and “Number of planes”. For example, if you choose a scan with 32 scan lines in your 2p control software (y = 32), you can then select 32 under “select y resolution” and the ETL will jump to a new plane every 32 lines, in perfect synch with the scan. Then you can define the number of planes. For example, if you choose 2 planes, it will execute 32 lines and depth 1, and then 32 lines at depth 2, and thereafter jump back to depth 1 etc.
Here, the specific depths it will jump to each time is defined in the window titled “planes”. Values entered in planes that are not used (e.g. plane 3 in a 2 plane configurations) will simply be ignored. For now, the GUI is configured for up to 6 planes to not clutter the GUI. However, it would be relatively straightforward for any experienced programmer to change this in the MATLAB code provided.
While this setup lets you set up straightforward multiplane scans, it can also execute some more “interesting” scan paths simply by playing with the numbers. For example, you can run a “step-scan” (i.e. half a scan at plane 1, and the other half in plane 2 – as for example shown for simultaneous eye-brain imaging in zebrafish in the accompanying MS). For this, taking our previous example, simply change the value of 32 to 16 under select y resolution. This will jump the ETL twice per frame and generate the intended effect).
Note also that there is no requirement for the scan planes to be evenly spaced, or event to be executed in any particular order. For example you could sample plane 1 at twice the rate as plane 2 and 3 by defining a 4-plane scan and setting z-values for the four planes accordingly.
Note: If you abort a scan at any time other than exactly at the end of a full frame, you may find that next time you run a multiplane or similar scan that the ETL and the scan mirrors are out of synch. This is because the GUI/Arduino only counts scan lines, and may thus have some remaining lines stored. To ensure this doesn’t happen, don’t update the Matlab GUI during scans. If the problem persists, simply stop the scan, and reload whatever ETL command configuration you want to execute. This will reset the counter.

XYZ scans To operate i.e XYZ mode (i.e. plane tilting), select your scan resolution (9), in the same manner for multiplane imaging (5). Select z-multiplication (10), the value of the z-shift of the last line. Z-multiplication works as follows: Say you use a 100x32 xy scan configuration in your scan mode and select a multiplication of 1. This means that for each new scan line, the ETL will be shifted by an ETL value of 1 to thus reach 32 by the last line (which corresponds to a shift of 32 in window 3). If for the same scan you will select a z-multiplication of 2, each line will be shifted by 2 to finally reach 64 by line 32 (and so on). Note that the product of the number of the number of scan lines and the multiplication factor cannot exceed 4,095.
In this way, you can also set-up a perfectly vertical scan. The simplest way might be to select a line-scan configuration in your scan software (i.e. y mirror silent). Alternatively, select an image scanning configuration and disconnect the y-mirror (just unplug it at the DAQ board - while it is not scanning!). The latter has the benefit that your scan software will display the XZ scan (as opposed to XY) as an image with Y corresponding to Z (some scan software solutions also do this for line scans so this may not be always necessary).

Note that in a “real” XZ mode (i.e. perfectly vertical), it is likely that the excitation volumes (point spread function) of subsequent z-lines will overlap because the psf is usually vertically elongated. This will give a blurred image. One way to ameliorate this effect is to slightly tilt the scan by engaging the Y mirror such that that subsequent psfs overlap less (i.e. a XYZ scan, where Y and Z are linked with the z-multiplication factor).

ETL software control: Half pipe scans
Upload ETL_HP.ino (Fig. 15) to the Arduino (instead of the “6planes” one used above). Similarly, launch the corresponding Matlab scripts GUI_HP.fig and GUI_HP.m (as above) and connect the Arduino to the GUI as before (window 1 and 2, Fig. 16).
The half-pipe GUI works in a very similar manner to the multiplane/xyz GUI.
As before, select your scan y-resolution (3). This GUI is set-up for 3 different modes (4). Standard z-shift of the entire plane (“just move”). Second, a ramp where the z-position updates linearly for each scan line up to half of the value defined under (3), and after that lineally decrease again (i.e. like a roof on a house). Third, a axial sine-wave scan. This operates like the ramp scan, except that now the z-value is updated in a sinusoidal fashion rather than linearly, which gives rise to a half-pipe-like z-scan pattern. The peak z-amplitude of these scan options is selected using slider (5) and confirmed using button (6). By definition, half-pipe and ramp scans always start from an ETL-value of zero.
ETL software control: Half pipe scans with 3 sinusoidal planes.
This mode operate on the same GUI as a standard half pike scan. Only one difference is on Arduino code. Upload ETL_HP_sin3planes.ino (Fig. 17) to the Arduino. This file is just a small modification of ETL_HP.ino described above. The difference is that third, sinusoidal scan mode operated on 3 planes imaging frame by frame. As using our ETL driver we are not able to supply negative current, now the value from slider 5 (fig. 16)

correspond to the flat, first plane, and two other planes are a sinusoidal positive half pipe with an amplitude at 2 values of slider 5, and negative sinusoidal half pipe with negative amplitude at 0.

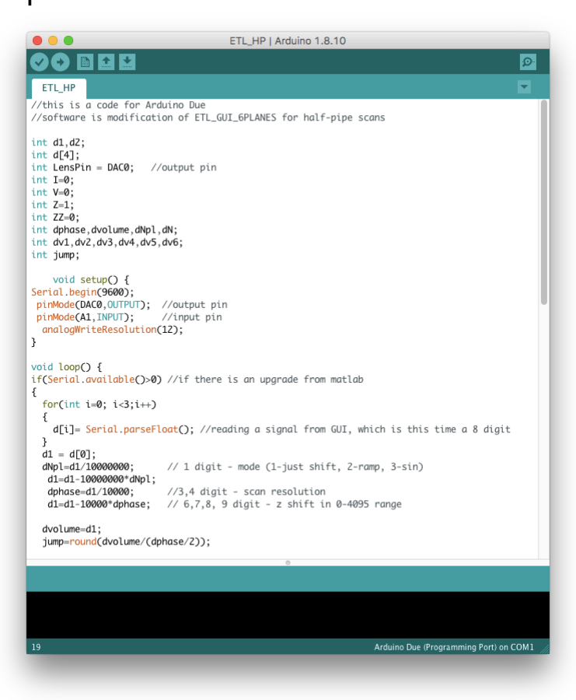
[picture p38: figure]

Fig. 15. Arduino code for Half-Pipe scans

//this is a code for Arduino Due
//software is modification of ETL_GUI_6PLANES for half-pipe scans int d1,d2;
int d[4];
int LensPin = DAC0; | //output pin
int I=0;
int V=0;
int Z=1;
int ZZ=0;
int dphase,dvolume,dNpl,dN; int dv1,dv2,dv3,dv4,dv5,dv6; int jump;
void setup() {
Serial.begin(9600);
pinMode(DAC0,OUTPUT); | //output pin
pinMode(A1,INPUT); | //input pin
analogWriteResolution(12);
}

void loop() {
if(Serial.available()>0) | //if there is an upgrade from matlab
{
for(int i=0; i<3;i++)
{
d[i]= Serial.parseFloat(); | //reading a signal from GUI, which is this time a 8 dig
}
d1 = d[0];
dNpl=d1/10000000; | // 1 digit - mode (1-just shift, 2-ramp, 3-sin)
d1=d1-10000000*dNpl;
dphase=d1/10000; | //3,4 digit - scan resolution
d1=d1-10000*dphase; | // 6,7,8, 9 digit - z shift in 0-4095 range
dvolume=d1;
jump=round(dvolume/(dphase/2));
I=0;
}
int sensVal=analogRead(A1);
switch (dNpl)
{
case 1: | // just shift
V=dvolume;
break;
case 2:{ | // ramp
if (sensVal<10){
Z=400;
}
if (sensVal+Z>1200){
Z=1;
I=I+Z;
V=I*jump;
}
if (I>=dphase/2){
V=(dphase/2)*jump-(I-(dphase/2))*jump; }
if (I==dphase){
I=0;
}
break;
}
case 3: | // sin
if (sensVal<10){
Z=400;
}
if (sensVal+Z>1200){
Z=1;
I=I+Z;
V=sin(radians(180*I/dphase))*dvolume; }
if (I==dphase){
I=0;
}
break;
}
analogWrite(LensPin,V);
}


Fig. 16. MATLAB GUI for Half-Pipe Scans.

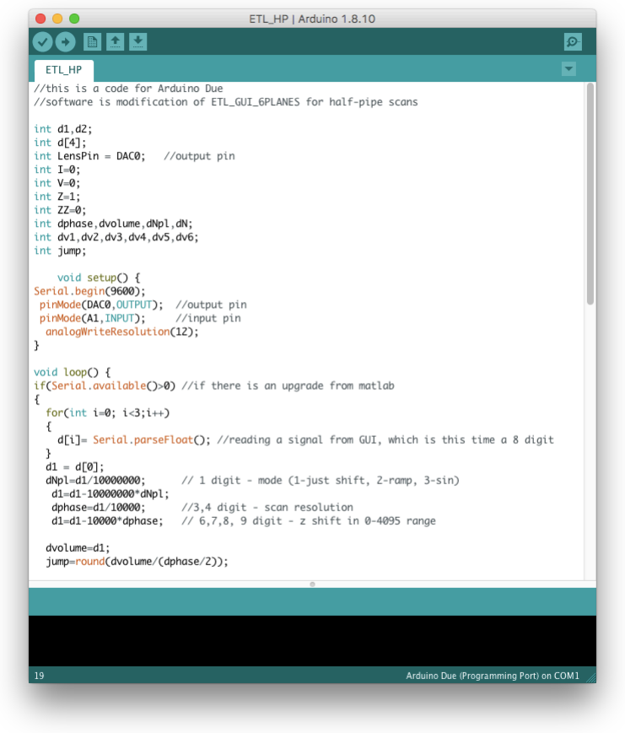
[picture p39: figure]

Fig. 17. Arduino code for Half-Pipe scans with sinusoidal 3planes imaging.

//this is a code for Arduino Due
//software is modification of ETL_GUI_6PLANES for half-pipe scans

int d1,d2;
int d[4];
int LensPin = DAC0; | //output pin
int I=0;
int V=0;
int Z=1;
int ZZ=0;
int dphase,dvolume,dNpl,dN; int dv1,dv2,dv3,dv4,dv5,dv6; int jump;

void setup() {
Serial.begin(9600);
pinMode(DAC0,OUTPUT); | //output pin
pinMode(A1,INPUT); | //input pin
analogWriteResolution(12);
}

void loop() {
if(Serial.available()>0) | //if there is an upgrade from matlab
{
for(int i=0; i<3;i++)
{
d[i]= Serial.parseFloat(); | //reading a signal from GUI, which is this time a 8 dig
}
d1 = d[0];
dNpl=d1/10000000; | // 1 digit - mode (1-just shift, 2-ramp, 3-sin)
d1=d1-10000000*dNpl;
dphase=d1/10000; | //3,4 digit - scan resolution
d1=d1-10000*dphase; | // 6,7,8, 9 digit - z shift in 0-4095 range

dvolume=d1;
jump=round(dvolume/(dphase/2));

I=0;
}

int sensVal=analogRead(A1);
switch (dNpl)
{
case 1: | // just shift
V=dvolume;
break;
case 2:{ | // ramp
if (sensVal<10){
Z=400;
}
if (sensVal+Z>1200){
Z=1;
I=I+Z;
V=I*jump;
}
if (I>=dphase/2){
V=(dphase/2)*jump-(I-(dphase/2))*jump; }
if (I==dphase){
I=0;

}
break;
}

case 3: // sin with up, down and flat (3planes) if (sensVal<10){
Z=400;
}
if (sensVal+Z>1200){
Z=1;
I=I+Z;
V=dvolume;
}
if (I>=dphase){
V=dvolume+sin(radians(180*I/dphase))*dvolume; }
if (I==dphase*3){
I=0;
}

break;
}
analogWrite(LensPin,V);
}

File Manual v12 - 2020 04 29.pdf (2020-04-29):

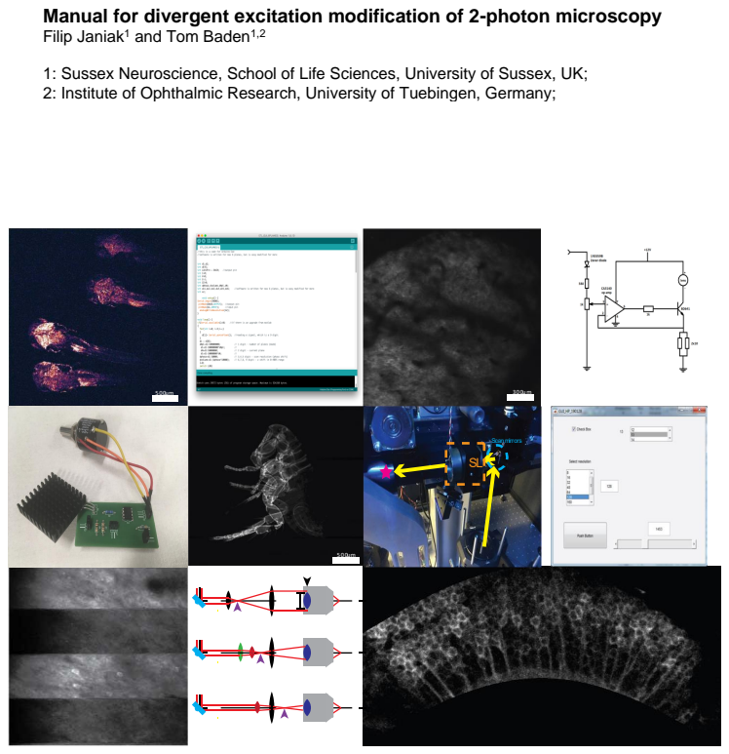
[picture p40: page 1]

Manual for divergent excitation modification of 2-photon microscopy
Filip Janiak¹ and Tom Baden¹,2

1: Sussex Neuroscience, School of Life Sciences, University of Sussex, UK;
2: Institute of Ophthalmic Research, University of Tuebingen, Germany;

A note on safety

Remember to always wear safety googles when working with lasers! Take off all hand-worn
jewellery and watches as these might reflect the beam into y u | e e el e’ eye .
Always work at the lowest possible laser power. And never, even with the safety glasses on, look straight into the laser beam!

What will be useful?

Tape measure, fixed fluorescence sample (i.e. a test-slide), laser viewing card

Definitions and helpful simplifications

Many of the optical elements in 2p microscopes, like the scan lens (SL), tube lens (TL) and objective (objective lens) tend to consist of multiple stacked lenses with different curvatures and thickness. For simplicity, we treat each of these as a single ideal lens.

In detail: There is a large set of parameters describing optical properties of such lenses, however for us important are only the following: principal planes (P, P’), focal planes (F, F’), surface vertices (V, V’), and three focal lengths: effective focal length (EFL), back focal length (BFL) and front focal length (FFL). For details on any of these, see also the following Wiki articles:

https://en.wikipedia.org/wiki/Cardinal_point_(optics) https://en.wikipedia.org/wiki/Focal_length

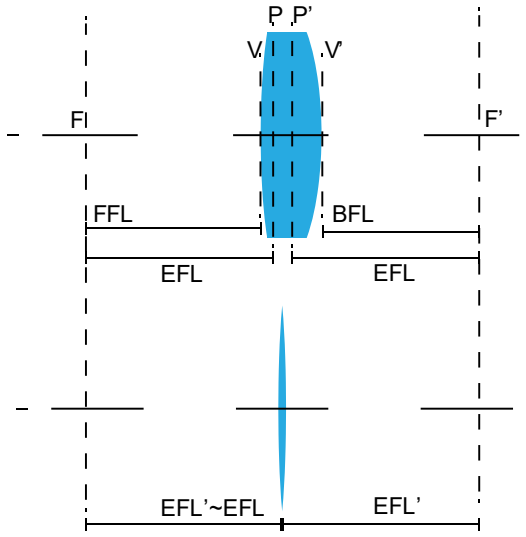
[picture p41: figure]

Fig 1. Thin lens approximation of a thick lens (a). Single thin lens approximation of two thick lenses (b).

In optical models, such constituent lenses can be replaced by a single, thin, ideal lens, and for simplicity this is what we are doing in all calculations and diagrams. This ideal lens has a negligible thickness, so principal points are located exactly in a centre of the lens, and effective, back and focal length are the same, and equal to EFL of thick lenses corrected by half of the thickness (EFL’ on fig 1). Typically, the thickness can be disregared if EFL>> thickness.

EFL

′ = EFL +

a
2

if (EFL ≫ a) EFL

′ ≅ EFL

To calculate effective focal length of two thin lenses, we can use:

1
EFL =

1
EFL1

+

1
EFL2

−

d
(EFL1)(EFL2)

Or just simply:
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
f1f2

See more on https://physics.stackexchange.com/questions/247617/how-is-focal-length-defined-for-a-two-lens-system-separated-by-a-distance-d (https://physics.stackexchange.com/questions/247617/how-is-focal-length-defined-for-a-two-lens-system-separated-by-a-distance-d)

This ideal lens is located in the back principal planes of complex lenses (which is usually in the centre of a given tube).

Initial steps: Obtaining all the key numbers of your specific setup.

This section is intended to help identify all key elements in your laser path between the scan mirrors and the sample plane, and to obtain concrete values for their relative distances and focal lengths etc..

1. Identify scan lens (SL). It should be the first lens ensemble after the scanning mirrors (from point of view of the laser source). Identify Tube Lens (TL), it should be the next one after SL. Measure the distance between them (D2).
2. If focal lengths and dimensions are unknown, carefully take out both lenses. Use gloves to avoid leaving smear-marks, and do not scratch them. Measure their focal distance (FSL,FTL), and their dimensions (ØSL, ØTL), for example as demonstrated here:

https://www.youtube.com/watch?v=joQw3_rM_jI

Fig 2. Sutter MOM setup with DL standard configuration. Location of SL (a), TL and objective (b). SL outlook (c) and mounting (d). TL outlook (e) and position from the side (f).

If you use a Sutter MOM setup, the SL model is VISIR 1534SPR136 from Leica (Fig. 2a), which is mounted in a WECO 77 tube (Fig. 2c). It has a focal length of 50 mm, and it is located 56.6 mm from second scan mirror. The thickness of the lens (which is made up of two biconvex lenses) is 43.1 mm. The external tube diameter is 38.2 mm, and the internal aperture diameter is 28.9 mm. It is easy to unscrew and take out (Fig. 2d).

However, in the Sutter MOM the TL (MXA22018, Nikon) is less readily accessible (Figs. 2b,f). It has a 200 mm focal length (Fig. 2e) and is positioned at a distance of 250 mm from the SL. The length of the TL tube is 29 mm, and it has a 36 mm aperture.

3. For your objective, check the magnification, nominal working distance, and size of the back aperture (Øobj). Measure the total distance between the objective’ back aperture and the SL.

Note: Microscope objectives are designed to correct for chromatic aberration at a specific distance D3 between TL and its back aperture OBA. For Zeiss objectives, D3 = 95 mm. (Philbert S. Tsai and David Kleinfeld, 2009).

In our setup, we use a Zeiss Objective W "Plan-Apochromat" 20x/1.0, 1.8 mm working distance.

In a standard diffraction limited (DL) configuration, the distance between SL and TL is equal to the sum of their focal distances D2=FSL+FTL. D3 is specified by the objective as discussed above.

4. Based on these numbers, calculate the distance D1 between the second scan mirror pivot point and SL that minimizes motion of laser beam (intensity fluctuation) on

objective back aperture:

Figure 3. DL configuration. Ideal lenses approximation (top), objective back aperture overfilling (left) and typical configuration with stacked lenses (down).


5. Check objective’ back aperture (OBA) filling factor (Øexc/Øobj). To do so, turn on a regular scan
mode | “ g z | ” ( .e. | l | e e
scan mirrors) without the objective in place. Use a
laser viewing card | e | e e e | e | e’
e u e | ul | e | e | e e u ’ | ll
( .e. e ze | e l e | el | e | e | e | e’
back aperture) (Fig. 3, 4). Alternatively, if your laser supports an alignment mode at a visible wavelength (typically low 700s of nm) you can also do this procedure with a piece of paper in place of the laser viewing card.

In a DL configuration, overfilling OBA by the excitation laser beam minimizes the lateral and axial size of the excitation spot (point spread function, psf), but also decreases effective excitation power delivered by the objective (Helmchen & Denk, 2005; Philbert S. Tsai and David Kleinfeld, 2009).

This manual describes how to change a setup from a DL configuration. Therefore, based on your data, check and calculate if your setup operates on DL settings.

If it is, go ahead to the next section. If it is not, try to understand why. There are two main possibilities. First, unintentional misalignment during a construction/mainlining or a using of the setup, which can be easily fixed to come back to DL configuration or apply a modification. Second, intentional changes from DL configuration. In this case you need to check why your setup is designed in this specific manner (e.g. if there are specific advantages/limitations). In this case, application of our modifications could be more complicated, but may still be possible.

We present two modifications to obtain a divergent excitation 2-photon setup leading to an expanded field of view (FOV) and excitation spot (point spread function, psf).

Throughout, we will be focussing on two parameters: Intermediary focal point (IFP) and
e | e | e’ | -filling factor (Fig. 5):
Intermediary focal point (IFP) position | Objective back aperture filling factor


Fig. 5. IPF positions (left) and objective back aperture filling factor (right) for 3 configurations DL(a), DBO1(b) and DBO2(c).

## DBO1 configuration

1. | “ | e ge | e | 1” ( | 1), the goal is to move the IFP
closer to the TL, yet without passing it, while simultaneously underfilling OBA (Fig. 6).
2. To assess the extent of any changes, use a fixed fluorescence sample. Prepare your setup for a standard experiment with DL configuration. Using lowest possible power find a suitable sample plane (one with obvious structure) and determine the original maximal FOV and working and working distance (e.g. by moving the sample side to side and checking when a particular image structure leaves the field of view).
3. Prepare setup to measure objective back aperture (OBA) filling factor (Øexc/Øobj) – see initial steps.
4. Completely remove SL from the system. Before implementing any modifications, remember to switch off the laser!

Sidenote: Why not simply shift the original SL? We can of course move the IPF closer to TL by simply shifting forward the SL. However, this will increase overfilling OBA (we are hoping to decrease this) which in turn will decrease effective excitation power on the sample plane (we are hoping to increase this).


Fig 6. Optical design of DL(a) and DBO1 configuration (b-d). Left part shows positions of the lens, right objective back aperture filling factor. (b and c) shows different positions on

L2 and in result different FOV and psf shape. (d) shows configuration (b) without thin lens approximation.

5. Insert new lenses in place of the SL. In our tested DBO1 solution for the Sutter MOM, we use 2 lenses in place of the SL: L1 and L2, with focal lengths 190 and 175 mm, respectively.

In our implementation, L1 is a modified Sutter MOM SL - VISIR 1534SPR136, Leica (Fig. 7b), and L2 is LA1229 from Thorlabs (Fig. 7c). This specific choice for L1 is one of convenience, but it can be equally be replaced by a new 190 mm lens.

DBO1 can also be achieved using a single lens. However, in this case, the OBA filling factor will be much smaller and difficult to control, and the psf will disproportionately inflate already for a small FOV increase.

For mounting L1, we use the original SL mount (as our L1 is a modified SL). For assembling and shifting L2, we use a 3D printed lens holder that fits into the existing tube that also holds the TL at its end (Fig. 6a). The 3D printable file Lens_holder.stl is found

on our GitHub.

Fig 7. Sutter MOM setup with DOB1 configuration. Location of L1 and L2 (a), L1 modified from Leica VISIR 1534SPR136 (b), L2 with custom design 3D printed holder (c)

6. Select the “right” L1 and L2 lenses for your setup.

Sketch out how you want the optical configuration of your setup to look like. Note original SL, TL and their apertures. Note existing holders for lenses and the physical
e | y y u e u ’ | e | .

For L1, use a lens with a focal distance FL1 = DL1, such that by itself, L1 sets up an IFP exactly at the centre of the TL. We use a 190 mm lens, positioned 190 mm in front of the TL.

If desired, you can also use an L1 with shorter or longer focal distance than DL1. However, if the focal distance is shorter, the range of FOV changes generated by shifting of L2 position decreases. In contrast, of L1 focal distance is longer than DL1, it will bring the IFP behind the TL, effectively resulting in DBO2 (discussed below). In this case we can shift between modification 1 and 2 mode by change a position of L2.

Make sure that the aperture (diameter) of L1 is suitable. It should be in similar range as the original SL (ØL1 ≈ ØSL) to make sure the incoming laser beam does not get clipped on the edges during scanning.

For L2, the focal length (FL2) should be in the range between FL1 and FL1/2. FL2 shortening introduce an overfilling of OBA, or even TL aperture, resulting in power lost and fluctuation of excitation intensity on FOV. FL2 extending decrease range of IFP and (Øexc/Øobj) changes.

On our setup, we use a 175 mm FL2, which is shifted along the laser path between 100 and 5 mm from TL.

Ultimately, the exact position vale of FL2 as well as the position of L2 relative to L1 and TL will dictate the position of the IFP, and thereby set the (Øexc/Øobj) factor, FOV and the size of the excitation psf.

If possible, choose an aperture of L2 that is similar to the one for L1 (ØL1 | ≈ | ØL2). In our
case it was not possible to use the exact same size, so we used the largest possible L2 diameter (25,5 mm) which just about fit into the 3D printed holder that was slotted into the tube that also held the TL.
7. Test the result of your changes and establish the range of FOV shifts achievable by shifting L2 up and down the laser path. Start by setting L2 as close as it is possible to L1 and take a scan of your fixed sample. Likely, working distance will be longer than in the original DL configuration so you will need to refocus. Note the difference of a working distance and check the maximal FOV size. Also, zoom in to assess spatial resolution. Now, shift L2 closer to TL and again check FOV and working distance. Both should increase. Note the range of changes that can be achieved with this configuration.

Remember to shift L2 only when you are not scanning and your laser is disabled!

If you find that working distance and FOV starts to decrease again at some point when shifting L2 closer to TL, it means that L2 is further away from L1 compared to L1’s focal distance. In this case, put L1 closer to TL or exchange it for the one with longer working distance.

8. As for 7, also check the objective filling factor (Øexc/Øobj) for a different positions of L2 (see initial steps paragraph). Shifting of L2 towards TL will increase underfilling (i.e.
ll | e e l e | lle | e le el | e | e | e’ | e u e), and should
result in an expansion of the psf.

If desired, you can try to keep a (Øexc/Øobj) constant even with increasing FOV by exchanging of L2 for one with shorter working distance as you shift it closer to TL. This effectively allows setting FOV somewhat independently of psf expansion (up to a point).

Sidenote: Remember that overfilling of OBA will reduce effective excitation power, and can also lead to uneven excitation power across the FOV.

9. As desired, you can also directly measure the excitation psf, for example by imaging fluorescent beads embedded in agarose. When doing so, remember to keep laser wavelength and excitation power at the sample plane approximately constant to ensure fair comparison (measured psf dimensions strongly depend on these factors). Note that excitation power at the sample plane should also increase as you decrease Øexc/Øobj, so it is best to directly measure this on the sample plane using a power meter.

## DBO2 configuration

1. In DBO2, goal is to move the IFP beyond the TL (but still in front of OBA), again while ensuring underfilling of OBA (Fig. 7). Most steps to set-up DBO2 are very similar to those required to set up DBO1. Therefore, first consult the description in DBO1. From here, implementation DBO2 will be straightforward:
2. Starting from a DBO1 configuration, remove L1 from the setup and replace L2 with L3. (If you start from a DL setup, simply remove the SL entirely, and find a way to mount L2/L3 in front of the TL).


Fig 8. Optical design of DL(top) and versions of DBO2 configurations (below). Left: positions of the lens(es), right: objective back aperture filling factor. Different positions of L3 and in result different FOV and psf shape. Bottom row shows configuration without thin lens approximation (see introductory definitions). To compare with DBO1 check Fig 6.

3. How to select L3? The goal of L3, depending on its position in front of TL, is to shift the IFP anywhere between the TL and OBA. In our setup we use a 200 mm focal length Ø1 plano convex lens (LA1708, Thorlabs) which is probably a good starting point for most optical configurations. L3 is assembled exactly like L2 in DBO1, using a 3D-printed holder. In our configuration we can slide it anywhere between just next to the TL and up to 10 cm in front of it.


Fig. 9. Sutter MOM setup with DOB2 configuration. Location of L3 (a) and L3 with custom design 3D printed holder (c)

Side note: If you remove all lenses except the TL and Objective (i.e. remove SL/L1/L2⁽*)), your parallel beam coming from the scan mirrors should come into focus beyond the objective back aperture (FTL is always bigger than D3). Accordingly, OBA will be illuminated by convergent beam. However, we want the beam to diverge, so you will need a L3 lens that is powerful enough to generate an IFP (just) before the laser beam reaches the objective.

Check always that the beam reaching the OBA is divergent, not convergent (for example with a laser viewing card).

Throughout, when choosing new lenses, make sure they have high transmission efficiency in the infrared range such that the laser beam does not get attenuated too much.

Remember to use the highest possible aperture of the lens. Of course, this factor will be limited by space in Your scope (in our cases size of the tube where L3 is moved. Selection of a too small aperture will likely result in inefficient collection of the excitation beam after the mirrors (as now there is no longer a SL to direct the beam onto L3).

Electrically Tunable Lens

In our setup we implemented an Electricaly Tunable Lens (ETL) for rapid axial focussing. Our ETL is an EL-16-40-TC20D, Optotune, controlled by a custom driver and custom written software (see GitHub).

ETL Optics


Fig 10. Sutter MOM setup with cage for ETL (a). View of the cage with ETL holder, and mirror reflecting excitation beam to scan mirrors (b), ETL on the holder (c) and ETL EL-16-40-TC20D by itself (d).

In our approach, we decided to use an ETL which operate in a range of -10 to +10 dpt. This means that it focuses from infinity (∞, no focus, parallel beam) to -10 cm for negative
current an | ∞ | +10 cm for positive current. If the ETL is not supplied by any current,
it does not strongly interfere light which is going through (according to the product manual, it introduces a negligible, long range focus).

The main idea is to locate the ETL far away from the objective (compare to original idea
presented by Grewe (G e e, | g , | ’ H , & Hel | e , | )). By changing the
’ focus from infinity to a positive value (supply positive current) we can then introduce a small convergence into the excitation beam before it hits the scan mirrors. This effectively elevates the imaging plane under the objective. In our solution, we are operating around 25% of a maximum ETL power, which give us an effective focus shift of up to 600 µm.

On our setup, the ETL in mounted horizontally on custom cage build from Thorlabs elements (more details in bill of materials, BOM). Fig. 10a presents the layout of the ETL holder on our Sutter MOM setup. We replaced the Sutter MOM-s original tube with mirror (which bounces the excitation beam from below onto the scan mirrors) by our cage including a new mirror. This new mirror can be adjusted in xyz directions, and in reflection angles, to help setup a perfectly vertical beam. The ETL holder is adjustable in x and y, and is located 20 cm below the first scan mirror.

ETL driver hardware


Fig 11. Top (a) and bottom (b) view of ETL driver printed circuit board (PCB). Schematic of electrical circuit (b) and photograph of the assembled driver (d). The Gerber files for producing the PCB are available on the project GitHub.

To control our ETL, we are using a custom designed current driver combined with an
Arduino Due microcontroller. | e | e ’ | e ll g l | ge e | e
signals that are line-synchronised with the 2-photon scan engine. For this, the Arduino Due reads a line-signal from the scan engine (e.g. a copy of the fast-mirror command, or a line-synchronised TTL pulse) to count lines. For this, the Arduino is reading such as
g l | l g | . | u | e, | g l | ly | y | e “ | g g l”
whic | e e | e | el Cell u g e | e | e ( e l e | l “ | ”
to reduce bleaching during retrace times, this has been discussed previously e.g. in Euler
e l. | 9 | luege ’ | e).
U | e | g | g l, e | u | “ u | l e ”, | exe u e | e
accordingly, based on a custom script controlled from a Matlab GUI (below). For this, the Arduino sends a driving signal through its Digital-Analog-Converter (DAC) output port into the custom driver board. On the Arduino side, this DAC signal is ranges from 0 to 4,095 (12 bit), which corresponds to a voltage range of 0.55 - 2.75 V, which serves as the sole scan input to the custom driver board. First, the 0.55 V offset (corresponding to 0 on the Arduino) is removed using an operational amplifier (op-amp). Next, the remaining signal is scaled using a potentiometer which allows defining the maximum current sent to the ET (which also indirectly defines its resolution). Finally, this signal is used to open a negative-positive-negative (NPN)-transistor, which works as a switch for a current from a separate +12V 0.42 A power supply.

Note that our current driver works only for a positive current, even if our ETL works also for the negative.

Note that we are using an additional Zener diode as a connector between Arduino output and our current driver input. Reason of using it was additional protection of current driver and ETL because of problems with series of unstable Arduino boards which we have been using (some of them temporary didn’t work properly). This Zener diode introduce additional voltage drop to the system, so it doesn’t need to be done on op-amp.

Figure 11a and b shows the PCB of our driver. PCB file ETL_driver_board.kicad_pcb is available for download on our GitHub. In addition, you will need the following electronic components (full details on BOM):

- Zener diode (1N5359B) (additional used as connector between Arduino and driver board – see note above)
- | R1 | Ω,
- | Ω | e | e e ,
- Op-amp CA3140EZ,
- R2 1 Ω,
- R3&R4 10 Ω.
- N6039G transistor
- 12 V 420 mA power supply.

All connection pins are labelled on the board (Arduino, +12, + (ETL), and GND for Arduino and power supply). The Pin next to + is a negative connection for ETL.

Note that in addition we attached a heat sink to the N6039G transistor which helps to dissipate heat if the driver is operated for prolonged periods of time (see photo in Fig. 11d).

Fig. 12. Our ETL driving circuit with labelled ETL, ETL driver, Arduino Due board and blanking signal.; ETL software control; Two pieces of custom code are required: An Arduino Script, and; the; Matlab; Graphical; User; Interface; (GUI).; Both; are; deposited on the project GitHub.; There are two versions of each,; scripts are for plane tilting and multiplane imaging, while the latter is for half-pipe scans.; Arduino:; ETL_HP.ino; ETL_GUI_6Planes.ino; Matlab:; Gui_HP.m; Gui_6planes.m (

Our software control is fully independent from the software used to control the 2P microscope (e.g. ScanImage, or in our case ScanM), meaning that it can in principle be seamlessly integrated with any working 2p system so long as a line-synch signal is available to be read by the Arduino.

To communicate with the Arduino and upload the script, download the Arduino integrated
development | environment | (IDE). | The | Arduino | IDE | is | freely | available | at
https://www.arduino.cc/en/main/software. Tutorials on how to connect the Arduino via serial link and upload scripts are widely available online, so we will not cover this step here. You only have to upload the script once (the Arduino stores it locally), but you will need to keep the Arduino connected to your computer prior to changing any scan configuration so as to allow the Matlab script to communicate with it (see below).


e | e | x 6 l | e , u | e | y | e | e

,

e | C | u u
e, | lu e, | l,
, | , | , | , | , | 6 | e | e | x 6 l | e , u | e | y | e
e
xz

e u ()
e | l. eg (96 | )
e( | C , U | U ) | u u
e( | , | U ) | u
l g | e e | lu | ( | )
l | ()
( e | l. | l | le() | ) | e e | u g | e | l
( | )
e | l. | e l | () | e | g | g | l, | 9 | g
l | g | u | e | l | e ( | e)
* | l
g | u e | l | e
*
e | , , | g | e | lu | ( | e | )
lu e | ( | e* | ) | 6, , , 9 | g | z | 9 | ge
( | )
e
lu e
e
lu e
e
lu e
e
lu e
e
lu e
e 6
6 | lu e
e | l | l g e | ( | ) | e | g l | g | g | l
( | l)
e | | xyz
( e | l | ) | e ge | e | lue e | . | CH C
C | C | U | U
xz | u | ( * | 9 | e)
* | lu e | z | xyz
( | e)
e | l | e
( e | l | )
e | l | lue e | e H | l | g | g | l | u | e u .
CH C | C | C | U | U
( e | l | )
( | e) | ge z | lu e
( | e* ) | ge z | lu e

e
e | l | e
( e | l | )
( e | l | )
( | e)
( | e* )
( | e* )

e
e | l | e
( e | l | )
( e | l | )
( | e)
( | e* )
( | e* )
( | e* )

e

e | l | e
( e | l | )
( e | l | )
( | e)
( | e* )
( | e* )
( | e* )
( | e* )

e

e 6 | 6 l | e
( e | l | )
( e | l | )

Fig 13. Arduino code with comments for multiplane and xyz imaging.

Our GUI is written in MATLAB (Mathworks), which is widely using in academia. If you do not have it on your computer, check if your institution has a licence for it. There is also a 30-day free trial version https://uk.mathworks.com/products/matlab.html.

ETL software control: Multiplane and XYZ imaging

First, upload | e | u | _GU _6 l e . | ( lle | “ | e | ” | u | )
the Arduino board. Once this is done, you can close the Arduino IDE.

Next, open MATLAB and launch Gui_6PLANES.fig and Gui_6PLANES.m (If you are unsure how to do this, look for an online tutorial how to launch code in MATLAB.). In short, put both files into a common folder, change the MATLAB path to this folder, and execute Gui_6PLANES.m. This should bring up the GUI (Fig. 14).

From within the MATLAB GUI, connect the Arduino. For this, select the serial (COM)-port to which the Arduino is connected (Fig. 14, list 1) (It will be the same that you previously
used to upload the Arduino script - y u | e u u e | e | y e | u | ’ C | -
port, search for one of the many tutorials online). In our cases it happens to be COM 13. Note: ensure that the COM port is not busy – this can easily happen if the Arduino IDE’s serial monitor happens to the open, or if it is still uploading the script.
Next tick the “ | ON” | e | x | e | to the ETL. This sets up an open serial
communication between Matlab and the Arduino (this also means that you can no longer communicate with the Arduino from elsewhere, e.g. the Arduino IDE. So, if you want to upload e.g. a different Arduino script, you need to untick the ETL ON box again).

From here, you are ready to start using the ETL in synch with the scan commands. Remember, in our implementation, the ETL can only lift the imaging plane, so the lowest position of your desired scan should be defined by the actual objective position (ETL at position 0)

e 6 | 6 l | e
( e | l | )
( e | l | )
( | e)
( | e* )
( | e* )
( | e* )
( | e* )
( | e*6)

6

e
e | gle l | e | | z e | g
lu e
e
l g | e( e | , ) | e | lue | u e | e

Search-z function. To statically change the z-plane of your scan, simply enter a value between 0-4,095 into window (3) and press button (4) to confirm. Each time you do this the GUI sends a command to the Arduino, which in turn will send a static driver signal to the ETL and thus shift the imaging plane. This function is useful to explore by hand which values entered into the GUI correspond to what kind of actual z-shift. Confirm that this
works by running any xy- | y u | e | g g | u | e (y u | ’
need to stop the scan for this). It may take a few seconds for any change to take effect.


Fig 14. MATLAB GUI for the multiplane and xyz imaging.

Z-shift calibration (optional). Use a structured fluorescence sample (e.g. a test-slide) that allows you to easily identify specific structures at different imaging depths. Prepare your setup for standard 2P imaging, find a suitable image plane without engaging the ETL (ETL
e e | e | “ ”). Now, put the maximum allowed value of 4,095 into window (3),
and push button (4). This should jump the imaging plane upwards, and potentially quite substantially so (in our case some 600 microns). Now go down in your sample using the objective and find the same imaging plane again. Take a note of the effective note the z-shift that you needed to use to compensate for the ETL. This is the maximum z-jump range possible with your configured optics and ETL-driver settings as defined by the potentionmeter (see driver). If this range is too small or too large for your purposes, rotate the potentiometer by a few turns and repeat the above. Once you are happy with the effective z-jump range, ensure that the dependency between the number entered into the GUI and the effective z-jump is approximately linear (it is very linear in our case, where we use ~25 max driving current on the ETL).

Scan-synchronised ETL commands. For any of the above procedures, the line-counting feature of our custom driver is not really used as the driver is just outputting static commands. However, for multiplane imaging, tilting the scan plane (xyz scans) or for halfpipe scans (see next chapter), the ETL must be synchronised to the scan mirrors with the line-synch connection (see driver chapter above).

Multiplane and staircase scans. Here, the control logic of our GUI is simple – for multiplane imaging it simply jumps the ETL to a new current (and hence effective focus position) once it counts a certain number of scan lines based on the values you enter
u e “ ele y e lu | ” | “ u | e | l e ”. | ex | le, | y u | e
with 32 scan lines in your 2p control software (y = 32), you can then select 32 under
“ ele y e lu | ” | e | ll u | e | l e e e y | l e , | e e | y
with the scan. Then you can define the number of planes. For example, if you choose 2 planes, it will execute 32 lines and depth 1, and then 32 lines at depth 2, and thereafter jump back to depth 1 etc.
He e, e | e | e | ll u | e | e | e e | e | le “ l e ”.
Values entered in planes that are not used (e.g. plane 3 in a 2 plane configurations) will simply be ignored. For now, the GUI is configured for up to 6 planes to not clutter the GUI. However, it would be relatively straightforward for any experienced programmer to change this in the MATLAB code provided.

While this setup lets you set up straightforward multiplane scans, it can also execute
e | e “ e e | g” | ly y l y g | e u | e . | ex | le,
y u | u | “ e - | ” ( .e. | l | l e , | e | e | l | l e | – as
for example shown for simultaneous eye-brain imaging in zebrafish in the accompanying MS). For this, taking our previous example, simply change the value of 32 to 16 under select y resolution. This will jump the ETL twice per frame and generate the intended effect).
Note also that there is no requirement for the scan planes to be evenly spaced, or event to be executed in any particular order. For example you could sample plane 1 at twice the rate as plane 2 and 3 by defining a 4-plane scan and setting z-values for the four planes accordingly.
Note: If you abort a scan at any time other than exactly at the end of a full frame, you may find that next time you run a multiplane or similar scan that the ETL and the scan mirrors are out of synch. This is because the GUI/Arduino only counts scan lines, and may thus have some remaining lines stored. To ensure this doesn’t happen, don’t update the Matlab GUI during scans. If the problem persists, simply stop the scan, and reload whatever ETL command configuration you want to execute. This will reset the counter.

XYZ scans To operate i.e XYZ mode (i.e. plane tilting), select your scan resolution (9), in the same manner for multiplane imaging (5). Select z-multiplication (10), the value of the z-shift of the last line. Z-multiplication works as follows: Say you use a 100x32 xy scan configuration in your scan mode and select a multiplication of 1. This means that for each new scan line, the ETL will be shifted by an ETL value of 1 to thus reach 32 by the last line (which corresponds to a shift of 32 in window 3). If for the same scan you will select a z-multiplication of 2, each line will be shifted by 2 to finally reach 64 by line 32 (and so on). Note that the product of the number of the number of scan lines and the multiplication factor cannot exceed 4,095.
In this way, you can also set-up a perfectly vertical scan. The simplest way might be to select a line-scan configuration in your scan software (i.e. y mirror silent). Alternatively, select an image scanning configuration and disconnect the y-mirror (just unplug it at the DAQ board - while it is not scanning!). The latter has the benefit that your scan software will display the XZ scan (as opposed to XY) as an image with Y corresponding to Z (some scan software solutions also do this for line scans so this may not be always necessary).

Note that in a “real” XZ mode (i.e. perfectly vertical), it is likely that the excitation volumes (point spread function) of subsequent z-lines will overlap because the psf is usually vertically elongated. This will give a blurred image. One way to ameliorate this effect is to slightly tilt the scan by engaging the Y mirror such that that subsequent psfs overlap less (i.e. a XYZ scan, where Y and Z are linked with the z-multiplication factor).

ETL software control: Half pipe scans
Upload ETL_HP.ino (Fig. 15) to the Arduino (instead o | e “6 l e ” | e u e | e).
Similarly, launch the corresponding Matlab scripts GUI_HP.fig and GUI_HP.m (as above) and connect the Arduino to the GUI as before (window 1 and 2, Fig. 16).

The half-pipe GUI works in a very similar manner to the multiplane/xyz GUI.

As before, select your scan y-resolution (3). This GUI is set-up for 3 different modes (4).
Standard z-shift of the entire plane (“ u | e”). Second, a ramp where the z-position
updates linearly for each scan line up to half of the value defined under (3), and after that lineally decrease again (i.e. like a roof on a house). Third, a axial sine-wave scan. This operates like the ramp scan, except that now the z-value is updated in a sinusoidal fashion rather than linearly, which gives rise to a half-pipe-like z-scan pattern. The peak z-amplitude of these scan options is selected using slider (5) and confirmed using button (6). By definition, half-pipe and ramp scans always start from an ETL-value of zero.

ETL software control: Half pipe scans with 3 sinusoidal planes.
This mode operates on the same GUI as a standard half pipe scan, with only a small difference in the Arduino code. Upload ETL_HP_sin3planes.ino (Fig. 17) to the Arduino. This file is just a small modification of ETL_HP.ino described above. As using our ETL driver we are not able to supply a negative current, now the value from slider 5 (Fig. 16) correspond to the flat, first plane, while the other planes are the sinusoidal positive half pipe with an amplitude at 2 values of slider 5, and negative sinusoidal half pipe with negative amplitude at 0. The latter Arduino modification is mainly intended as an example how a small change in the Arduino code can be quickly used to define new scan-paths.


Fig. 15. Arduino code for Half-Pipe scans

e | u | ue
e | _GU _6 | l | e

,

e | C | u u
e, | lu e, | l,
, | , | , | , | , | 6
u

e u ()
e | l. eg (96 | )
e( | C , U | U ) | u u
e( | , | U ) | u
l g | e e | lu | ( )
l | ()
( e | l. | l | le() ) | e e | u g | e | l
( | )
e | l. | e l | () | e | g | g | l | GU , | e | g
l | g | e ( u | , | , | )
* | l
e | , | g | e | lu
* | e | 6, , , 9 | g | z | 9 | ge

lu e
u | u | ( | lu e ( | e ))
e | l | l g e | ( | )
( | l)
e | u
| lu e
e

e
( e | l | )
( e | l | )

* u

( | e )
( | e )* u | ( ( | e ))* u
( | e)

e

e
( e | l | )
( e | l | )
( | ( | * | e))* | lu e
( | e)

e

l g | e( e | , )


Fig. 16. MATLAB GUI for Half-Pipe Scans.


Fig. 17. Arduino code for Half-Pipe scans for sinusoidal 3 plane-imaging.

e | u | ue
e | _GU _6 | l | e

,

e | C | u u
e, | lu e, | l,
, | , | , | , | , | 6
u

e u ()
e | l. eg (96 | )
e( | C , U | U ) | u u
e( | , | U ) | u
l g | e e | lu | ( )
l | ()
( e | l. | l | le() ) | e e | u g | e | l
( | | | )
e | l. | e l | () | e | g | g | l | GU , | e | g
l | g | e ( u | , | , | )
* | l
e | , | g | e | lu
* | e | 6, , , 9 | g | z | 9 | ge

lu e
u | u | ( | lu e ( | e ))
e | l | l g e | ( | )
( | l)
e | u
| lu e
e

e
( e | l | )
( e | l | )

* u

( | e )
( | e )* u | ( ( | e ))* u
( | e)

e

e | u , | l | ( l | e )
( e | l | )
( e | l | )

lu e

( | e)
lu e | ( | ( | * | e))* | lu e
( | e* )

e

l g | e( e | , )

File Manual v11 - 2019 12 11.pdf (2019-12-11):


Manual for divergent excitation modification of 2-photon microscopy
Filip Janiak¹ and Tom Baden¹,2

1: Sussex Neuroscience, School of Life Sciences, University of Sussex, UK;
2: Institute of Ophthalmic Research, University of Tuebingen, Germany;

A note on safety

Remember to always wear safety googles when working with lasers! Take off all hand-worn
jewellery and watches as these might reflect the beam into y u | e e el e’ eye .
Always work at the lowest possible laser power. And never, even with the safety glasses on, look straight into the laser beam!

What will be useful?

Tape measure, fixed fluorescence sample (i.e. a test-slide), laser viewing card

Definitions and helpful simplifications

Many of the optical elements in 2p microscopes, like the scan lens (SL), tube lens (TL) and objective (objective lens) tend to consist of multiple stacked lenses with different curvatures and thickness. For simplicity, we treat each of these as a single ideal lens.

In detail: There is a large set of parameters describing optical properties of such lenses, however for us important are only the following: principal planes (P, P’), focal planes (F, F’), surface vertices (V, V’), and three focal lengths: effective focal length (EFL), back focal length (BFL) and front focal length (FFL). For details on any of these, see also the following Wiki articles:

https://en.wikipedia.org/wiki/Cardinal_point_(optics) https://en.wikipedia.org/wiki/Focal_length


Fig 1. Thin lens approximation of a thick lens (a). Single thin lens approximation of two thick lenses (b).

In optical models, such constituent lenses can be replaced by a single, thin, ideal lens, and for simplicity this is what we are doing in all calculations and diagrams. This ideal lens has a negligible thickness, so principal points are located exactly in a centre of the lens, and effective, back and focal length are the same, and equal to EFL of thick lenses corrected by half of the thickness (EFL’ on fig 1). Typically, the thickness can be disregared if EFL>> thickness.

EFL

′ = EFL +

a
2

if (EFL ≫ a) EFL

′ ≅ EFL

To calculate effective focal length of two thin lenses, we can use:

1
EFL =

1
EFL1

+

1
EFL2

−

d
(EFL1)(EFL2)

Or just simply:
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
f1f2

See more on https://physics.stackexchange.com/questions/247617/how-is-focal-length-defined-for-a-two-lens-system-separated-by-a-distance-d (https://physics.stackexchange.com/questions/247617/how-is-focal-length-defined-for-a-two-lens-system-separated-by-a-distance-d)

This ideal lens is located in the back principal planes of complex lenses (which is usually in the centre of a given tube).

Initial steps: Obtaining all the key numbers of your specific setup.

This section is intended to help identify all key elements in your laser path between the scan mirrors and the sample plane, and to obtain concrete values for their relative distances and focal lengths etc..

1. Identify scan lens (SL). It should be the first lens ensemble after the scanning mirrors (from point of view of the laser source). Identify Tube Lens (TL), it should be the next one after SL. Measure the distance between them (D2).
2. If focal lengths and dimensions are unknown, carefully take out both lenses. Use gloves to avoid leaving smear-marks, and do not scratch them. Measure their focal distance (FSL,FTL), and their dimensions (ØSL, ØTL), for example as demonstrated here:

https://www.youtube.com/watch?v=joQw3_rM_jI

Fig 2. Sutter MOM setup with DL standard configuration. Location of SL (a), TL and objective (b). SL outlook (c) and mounting (d). TL outlook (e) and position from the side (f).

If you use a Sutter MOM setup, the SL model is VISIR 1534SPR136 from Leica (Fig. 2a), which is mounted in a WECO 77 tube (Fig. 2c). It has a focal length of 50 mm, and it is located 56.6 mm from second scan mirror. The thickness of the lens (which is made up of two biconvex lenses) is 43.1 mm. The external tube diameter is 38.2 mm, and the internal aperture diameter is 28.9 mm. It is easy to unscrew and take out (Fig. 2d).

However, in the Sutter MOM the TL (MXA22018, Nikon) is less readily accessible (Figs. 2b,f). It has a 200 mm focal length (Fig. 2e) and is positioned at a distance of 250 mm from the SL. The length of the TL tube is 29 mm, and it has a 36 mm aperture.

3. For your objective, check the magnification, nominal working distance, and size of the back aperture (Øobj). Measure the total distance between the objective’ back aperture and the SL.

Note: Microscope objectives are designed to correct for chromatic aberration at a specific distance D3 between TL and its back aperture OBA. For Zeiss objectives, D3 = 95 mm. (Philbert S. Tsai and David Kleinfeld, 2009).

In our setup, we use a Zeiss Objective W "Plan-Apochromat" 20x/1.0, 1.8 mm working distance.

In a standard diffraction limited (DL) configuration, the distance between SL and TL is equal to the sum of their focal distances D2=FSL+FTL. D3 is specified by the objective as discussed above.

4. Based on these numbers, calculate the distance D1 between the second scan mirror pivot point and SL that minimizes motion of laser beam (intensity fluctuation) on

objective back aperture:

Figure 3. DL configuration. Ideal lenses approximation (top), objective back aperture overfilling (left) and typical configuration with stacked lenses (down).


5. Check objective’ back aperture (OBA) filling factor (Øexc/Øobj). To do so, turn on a regular scan
mode | “ g z | ” ( .e. | l | e e
scan mirrors) without the objective in place. Use a
laser viewing card | e | e e e | e | e’
e u e | ul | e | e | e e u ’ | ll
( .e. e ze | e l e | el | e | e | e | e’
back aperture) (Fig. 3, 4). Alternatively, if your laser supports an alignment mode at a visible wavelength (typically low 700s of nm) you can also do this procedure with a piece of paper in place of the laser viewing card.

In a DL configuration, overfilling OBA by the excitation laser beam minimizes the lateral and axial size of the excitation spot (point spread function, psf), but also decreases effective excitation power delivered by the objective (Helmchen & Denk, 2005; Philbert S. Tsai and David Kleinfeld, 2009).

This manual describes how to change a setup from a DL configuration. Therefore, based on your data, check and calculate if your setup operates on DL settings.

If it is, go ahead to the next section. If it is not, try to understand why. There are two main possibilities. First, unintentional misalignment during a construction/mainlining or a using of the setup, which can be easily fixed to come back to DL configuration or apply a modification. Second, intentional changes from DL configuration. In this case you need to check why your setup is designed in this specific manner (e.g. if there are specific advantages/limitations). In this case, application of our modifications could be more complicated, but may still be possible.

We present two modifications to obtain a divergent excitation 2-photon setup leading to an expanded field of view (FOV) and excitation spot (point spread function, psf).

Throughout, we will be focussing on two parameters: Intermediary focal point (IFP) and
e | e | e’ | -filling factor (Fig. 5):
Intermediary focal point (IFP) position | Objective back aperture filling factor


Fig. 5. IPF positions (left) and objective back aperture filling factor (right) for 3 configurations DL(a), DBO1(b) and DBO2(c).

## DBO1 configuration

1. | “ | e ge | e | 1” ( | 1), the goal is to move the IFP
closer to the TL, yet without passing it, while simultaneously underfilling OBA (Fig. 6).
2. To assess the extent of any changes, use a fixed fluorescence sample. Prepare your setup for a standard experiment with DL configuration. Using lowest possible power find a suitable sample plane (one with obvious structure) and determine the original maximal FOV and working and working distance (e.g. by moving the sample side to side and checking when a particular image structure leaves the field of view).
3. Prepare setup to measure objective back aperture (OBA) filling factor (Øexc/Øobj) – see initial steps.
4. Completely remove SL from the system. Before implementing any modifications, remember to switch off the laser!

Sidenote: Why not simply shift the original SL? We can of course move the IPF closer to TL by simply shifting forward the SL. However, this will increase overfilling OBA (we are hoping to decrease this) which in turn will decrease effective excitation power on the sample plane (we are hoping to increase this).


Fig 6. Optical design of DL(a) and DBO1 configuration (b-d). Left part shows positions of the lens, right objective back aperture filling factor. (b and c) shows different positions on

L2 and in result different FOV and psf shape. (d) shows configuration (b) without thin lens approximation.

5. Insert new lenses in place of the SL. In our tested DBO1 solution for the Sutter MOM, we use 2 lenses in place of the SL: L1 and L2, with focal lengths 190 and 175 mm, respectively.

In our implementation, L1 is a modified Sutter MOM SL - VISIR 1534SPR136, Leica (Fig. 7b), and L2 is LA1229 from Thorlabs (Fig. 7c). This specific choice for L1 is one of convenience, but it can be equally be replaced by a new 190 mm lens.

DBO1 can also be achieved using a single lens. However, in this case, the OBA filling factor will be much smaller and difficult to control, and the psf will disproportionately inflate already for a small FOV increase.

For mounting L1, we use the original SL mount (as our L1 is a modified SL). For assembling and shifting L2, we use a 3D printed lens holder that fits into the existing tube that also holds the TL at its end (Fig. 6a). The 3D printable file Lens_holder.stl is found

on our GitHub.

Fig 7. Sutter MOM setup with DOB1 configuration. Location of L1 and L2 (a), L1 modified
from Leica | VISIR 1534SPR136 | (b), L2 with custom design 3D printed holder (c)
6. Select the “right” L1 and L2 lenses for your setup.

Sketch out how you want the optical configuration of your setup to look like. Note original SL, TL and their apertures. Note existing holders for lenses and the physical
e | y y u e u ’ | e | .

For L1, use a lens with a focal distance FL1 = DL1, such that by itself, L1 sets up an IFP exactly at the centre of the TL. We use a 190 mm lens, positioned 190 mm in front of the TL.

If desired, you can also use an L1 with shorter or longer focal distance than DL1. However, if the focal distance is shorter, the range of FOV changes generated by shifting of L2 position decreases. In contrast, of L1 focal distance is longer than DL1, it will bring the IFP behind the TL, effectively resulting in DBO2 (discussed below). In this case we can shift between modification 1 and 2 mode by change a position of L2.

Make sure that the aperture (diameter) of L1 is suitable. It should be in similar range as the original SL (ØL1 ≈ ØSL) to make sure the incoming laser beam does not get clipped on the edges during scanning.

For L2, the focal length (FL2) should be in the range between FL1 and FL1/2. FL2 shortening introduce an overfilling of OBA, or even TL aperture, resulting in power lost and fluctuation of excitation intensity on FOV. FL2 extending decrease range of IFP and (Øexc/Øobj) changes.

On our setup, we use a 175 mm FL2, which is shifted along the laser path between 100 and 5 mm from TL.

Ultimately, the exact position vale of FL2 as well as the position of L2 relative to L1 and TL will dictate the position of the IFP, and thereby set the (Øexc/Øobj) factor, FOV and the size of the excitation psf.

If possible, choose an aperture of L2 that is similar to the one for L1 (ØL1 | ≈ | ØL2). In our
case it was not possible to use the exact same size, so we used the largest possible L2 diameter (25,5 mm) which just about fit into the 3D printed holder that was slotted into the tube that also held the TL.
7. Test the result of your changes and establish the range of FOV shifts achievable by shifting L2 up and down the laser path. Start by setting L2 as close as it is possible to L1 and take a scan of your fixed sample. Likely, working distance will be longer than in the original DL configuration so you will need to refocus. Note the difference of a working distance and check the maximal FOV size. Also, zoom in to assess spatial resolution. Now, shift L2 closer to TL and again check FOV and working distance. Both should increase. Note the range of changes that can be achieved with this configuration.

Remember to shift L2 only when you are not scanning and your laser is disabled!

If you find that working distance and FOV starts to decrease again at some point when shifting L2 closer to TL, it means that L2 is further away from L1 compared to L1’s focal distance. In this case, put L1 closer to TL or exchange it for the one with longer working distance.

8. As for 7, also check the objective filling factor (Øexc/Øobj) for a different positions of L2 (see initial steps paragraph). Shifting of L2 towards TL will increase underfilling (i.e.
ll | e e l e | lle | e le el | e | e | e’ | e u e), and should
result in an expansion of the psf.

If desired, you can try to keep a (Øexc/Øobj) constant even with increasing FOV by exchanging of L2 for one with shorter working distance as you shift it closer to TL. This effectively allows setting FOV somewhat independently of psf expansion (up to a point).

Sidenote: Remember that overfilling of OBA will reduce effective excitation power, and can also lead to uneven excitation power across the FOV.

9. As desired, you can also directly measure the excitation psf, for example by imaging fluorescent beads embedded in agarose. When doing so, remember to keep laser wavelength and excitation power at the sample plane approximately constant to ensure fair comparison (measured psf dimensions strongly depend on these factors). Note that excitation power at the sample plane should also increase as you decrease Øexc/Øobj, so it is best to directly measure this on the sample plane using a power meter.

## DBO2 configuration

1. In DBO2, goal is to move the IFP beyond the TL (but still in front of OBA), again while ensuring underfilling of OBA (Fig. 7). Most steps to set-up DBO2 are very similar to those required to set up DBO1. Therefore, first consult the description in DBO1. From here, implementation DBO2 will be straightforward:
2. Starting from a DBO1 configuration, remove L1 from the setup and replace L2 with L3. (If you start from a DL setup, simply remove the SL entirely, and find a way to mount L2/L3 in front of the TL).


Fig 8. Optical design of DL(top) and versions of DBO2 configurations (below). Left: positions of the lens(es), right: objective back aperture filling factor. Different positions of L3 and in result different FOV and psf shape. Bottom row shows configuration without thin lens approximation (see introductory definitions). To compare with DBO1 check Fig 6.

3. How to select L3? The goal of L3, depending on its position in front of TL, is to shift the IFP anywhere between the TL and OBA. In our setup we use a 200 mm focal length Ø1 plano convex lens (LA1708, Thorlabs) which is probably a good starting point for most optical configurations. L3 is assembled exactly like L2 in DBO1, using a 3D-printed holder. In our configuration we can slide it anywhere between just next to the TL and up to 10 cm in front of it.


Fig. 9. Sutter MOM setup with DOB2 configuration. Location of L3 (a) and L3 with custom design 3D printed holder (c)

Side note: If you remove all lenses except the TL and Objective (i.e. remove SL/L1/L2⁽*)), your parallel beam coming from the scan mirrors should come into focus beyond the objective back aperture (FTL is always bigger than D3). Accordingly, OBA will be illuminated by convergent beam. However, we want the beam to diverge, so you will need a L3 lens that is powerful enough to generate an IFP (just) before the laser beam reaches the objective.

Check always that the beam reaching the OBA is divergent, not convergent (for example with a laser viewing card).

Throughout, when choosing new lenses, make sure they have high transmission efficiency in the infrared range such that the laser beam does not get attenuated too much.

Remember to use the highest possible aperture of the lens. Of course, this factor will be limited by space in Your scope (in our cases size of the tube where L3 is moved. Selection of a too small aperture will likely result in inefficient collection of the excitation beam after the mirrors (as now there is no longer a SL to direct the beam onto L3).

Electrically Tunable Lens

In our setup we implemented an Electricaly Tunable Lens (ETL) for rapid axial focussing. Our ETL is an EL-16-40-TC20D, Optotune, controlled by a custom driver and custom written software (see GitHub).

ETL Optics


Fig 10. Sutter MOM setup with cage for ETL (a). View of the cage with ETL holder, and mirror reflecting excitation beam to scan mirrors (b), ETL on the holder (c) and ETL EL-16-40-TC20D by itself (d).

In our approach, we decided to use an ETL which operate in a range of -10 to +10 dpt. This means that it focuses from infinity (∞, no focus, parallel beam) to -10 cm for negative
current an | ∞ | +10 cm for positive current. If the ETL is not supplied by any current,
it does not strongly interfere light which is going through (according to the product manual, it introduces a negligible, long range focus).

The main idea is to locate the ETL far away from the objective (compare to original idea
presented by Grewe (G e e, | g , | ’ H , & Hel | e , | )). By changing the
’ focus from infinity to a positive value (supply positive current) we can then introduce a small convergence into the excitation beam before it hits the scan mirrors. This effectively elevates the imaging plane under the objective. In our solution, we are operating around 25% of a maximum ETL power, which give us an effective focus shift of up to 600 µm.

On our setup, the ETL in mounted horizontally on custom cage build from Thorlabs elements (more details in bill of materials, BOM). Fig. 10a presents the layout of the ETL holder on our Sutter MOM setup. We replaced the Sutter MOM-s original tube with mirror (which bounces the excitation beam from below onto the scan mirrors) by our cage including a new mirror. This new mirror can be adjusted in xyz directions, and in reflection angles, to help setup a perfectly vertical beam. The ETL holder is adjustable in x and y, and is located 20 cm below the first scan mirror.

ETL driver hardware


Fig 11. Top (a) and bottom (b) view of ETL driver printed circuit board (PCB). Schematic of electrical circuit (b) and photograph of the assembled driver (d). The Gerber files for producing the PCB are available on the project GitHub.

To control our ETL, we are using a custom designed current driver combined with an
Arduino Due microcontroller. | e | e ’ | e ll g l | ge e | e
signals that are line-synchronised with the 2-photon scan engine. For this, the Arduino Due reads a line-signal from the scan engine (e.g. a copy of the fast-mirror command, or a line-synchronised TTL pulse) to count lines. For this, the Arduino is reading such as
g l | l g | . | u | e, | g l | ly | y | e “ | g g l”
whic | e e | e | el Cell u g e | e | e ( e l e | l “ | ”
to reduce bleaching during retrace times, this has been discussed previously e.g. in Euler
e l. | 9 | luege ’ | e).
U | e | g | g l, e | u | “ u | l e ”, | exe u e | e
accordingly, based on a custom script controlled from a Matlab GUI (below). For this, the Arduino sends a driving signal through its Digital-Analog-Converter (DAC) output port into the custom driver board. On the Arduino side, this DAC signal is ranges from 0 to 4,095 (12 bit), which corresponds to a voltage range of 0.55 - 2.75 V, which serves as the sole scan input to the custom driver board. First, the 0.55 V offset (corresponding to 0 on the Arduino) is removed using an operational amplifier (op-amp). Next, the remaining signal is scaled using a potentiometer which allows defining the maximum current sent to the ET (which also indirectly defines its resolution). Finally, this signal is used to open a negative-positive-negative (NPN)-transistor, which works as a switch for a current from a separate +12V 0.42 A power supply.

Note that our current driver works only for a positive current, even if our ETL works also for the negative.

Figure 11a and b shows the PCB of our driver. PCB file ETL_driver_board.kicad_pcb is available for download on our GitHub. In addition, you will need the following electronic components (full details on BOM):

- Zener diode (1N5359B),
- | R1 | Ω,
- | Ω | e | e e ,
- Op-amp CA3140EZ,
- R2 1 Ω,
- R3&R4 10 Ω.
- N6039G transistor
- 12 V 420 mA power supply.

All connection pins are labelled on the board (Arduino, +12, + (ETL), and GND for Arduino and power supply). The Pin next to + is a negative connection for ETL.

Note that in addition we attached a heat sink to the N6039G transistor which helps to dissipate heat if the driver is operated for prolonged periods of time (see photo in Fig. 11d).

Fig. 12. Our ETL driving circuit with labelled ETL, ETL driver, Arduino Due board and blanking signal.; ETL software control; Two pieces of custom code are required: An Arduino Script, and; the; Matlab; Graphical; User; Interface; (GUI).; Both; are; deposited on the project GitHub.; There are two versions of each,; scripts are for plane tilting and multiplane imaging, while the latter is for half-pipe scans.; Arduino:; ETL_HP.ino; ETL_GUI_6Planes.ino; Matlab:; Gui_HP.m; Gui_6planes.m (

Our software control is fully independent from the software used to control the 2P microscope (e.g. ScanImage, or in our case ScanM), meaning that it can in principle be seamlessly integrated with any working 2p system so long as a line-synch signal is available to be read by the Arduino.

To communicate with the Arduino and upload the script, download the Arduino integrated
development | environment | (IDE). | The | Arduino | IDE | is | freely | available | at
https://www.arduino.cc/en/main/software. Tutorials on how to connect the Arduino via serial link and upload scripts are widely available online, so we will not cover this step here. You only have to upload the script once (the Arduino stores it locally), but you will need to keep the Arduino connected to your computer prior to changing any scan configuration so as to allow the Matlab script to communicate with it (see below).

Our GUI is written in MATLAB (Mathworks), which is widely using in academia. If you do not have it on your computer, check if your institution has a licence for it. There is also a 30-day free trial version https://uk.mathworks.com/products/matlab.html.


e | e | x 6 l | e , u | e | y | e | e

,

e | C | u u
e, | lu e, | l,
, | , | , | , | , 6 | e | e | x 6 l | e , u | e | y | e
e
xz

e u ()
e | l. eg (96 | )
e( | C , U | U ) | u u
e( | , | U ) | u
l g | e e | lu | ( | )
l | ()
( e | l. | l | le() | ) | e e | u g | e | l
( | )
e | l. | e l | () | e | g | g | l, | 9 | g
l | g | u | e | l | e ( | e)
* | l
g | u e | l | e
*
e | , , | g | e | lu | ( | e | )
lu e | ( | e* | ) | 6, , , 9 | g | z | 9 | ge
( | )
e
lu e
e
lu e
e
lu e
e
lu e
e
lu e
e 6
6 | lu e
e | l | l g e | ( | ) | e | g l | g | g | l
( | l)
e | xyz
( e | l | ) | e ge | e | lue e | . | CH C
C | C | U | U
xz | u | ( * | 9 | e)
* | lu e | z | xyz
( | e)
e | l | e
( e | l | )
e | l | lue e e H | l | g | g | l | u | e u .
CH C | C | C | U | U
( e | l | )
( | e) | ge z | lu e
( | e* ) | ge z | lu e

e
e | l | e
( e | l | )
( e | l | )
( | e)
( | e* )
( | e* )

e
e | l | e
( e | l | )
( e | l | )
( | e)
( | e* )
( | e* )
( | e* )

e

e | l | e
( e | l | )
( e | l | )
( | e)
( | e* )
( | e* )
( | e* )
( | e* )

e

e 6 | 6 l | e
( e | l | )
( e | l | )

Fig 13. Arduino code with comments for multiplane and xyz imaging.

ETL software control: Multiplane and XYZ imaging

First, upload | e | u | _GU _6 l e . | ( lle | “ | e | ” | u | )
the Arduino board. Once this is done, you can close the Arduino IDE.

Next, open MATLAB and launch Gui_6PLANES.fig and Gui_6PLANES.m (If you are unsure how to do this, look for an online tutorial how to launch code in MATLAB.). In short, put both files into a common folder, change the MATLAB path to this folder, and execute Gui_6PLANES.m. This should bring up the GUI (Fig. 14).
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

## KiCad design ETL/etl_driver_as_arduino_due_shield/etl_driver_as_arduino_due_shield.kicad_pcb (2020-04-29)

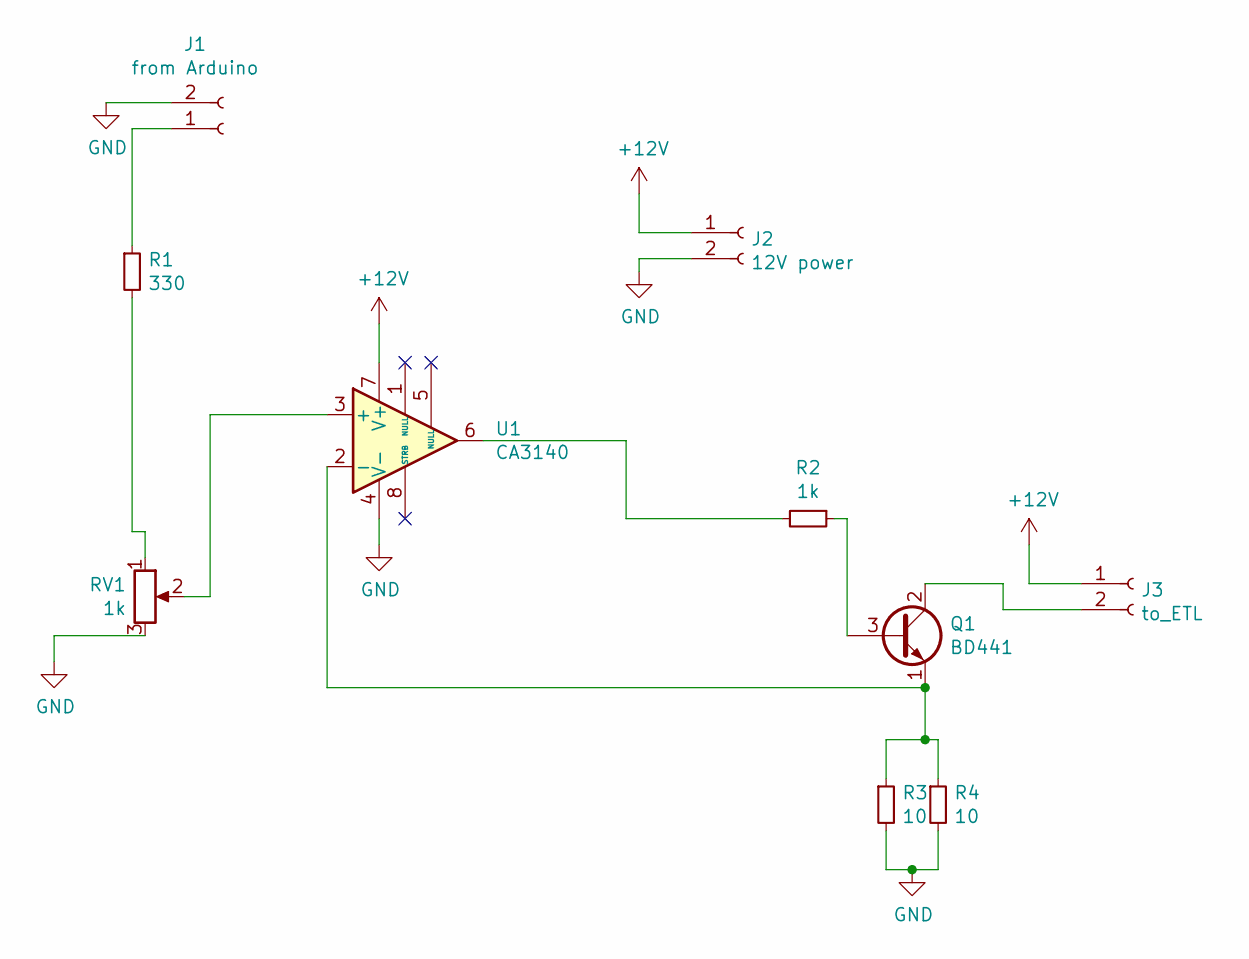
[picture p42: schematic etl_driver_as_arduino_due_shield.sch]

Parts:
J1: from Arduino; PinHeader_1x02_P2.54mm_Vertical
J2: 12V power; PinHeader_1x02_P2.54mm_Vertical
J3: to_ETL; PinHeader_1x02_P2.54mm_Vertical
Q1: BD441; TO-126-3_Vertical
R1: 330; R_Axial_DIN0207_L6.3mm_D2.5mm_P10.16mm_Horizontal
R2: 1k; R_Axial_DIN0207_L6.3mm_D2.5mm_P10.16mm_Horizontal
R3, R4: 10; R_Axial_DIN0207_L6.3mm_D2.5mm_P10.16mm_Horizontal
RV1: 1k; Potentiometer_ACP_CA9-H3,8_Horizontal
U1: CA3140; DIP-8_W7.62mm_Socket

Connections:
+12V: J2.1, J3.1, U1.7 (V+)
GND: J1.2, J2.2, R3.2, R4.2, RV1.3, U1.4 (V-)
unnamed: J1.1, R1.1
unnamed: J3.2, Q1.2 (C)
unnamed: Q1.1 (E), R3.1, R4.1, U1.2 (-)
unnamed: Q1.3 (B), R2.1
unnamed: R1.2, RV1.1
unnamed: R2.2, U1.6
unnamed: RV1.2, U1.3 (+)

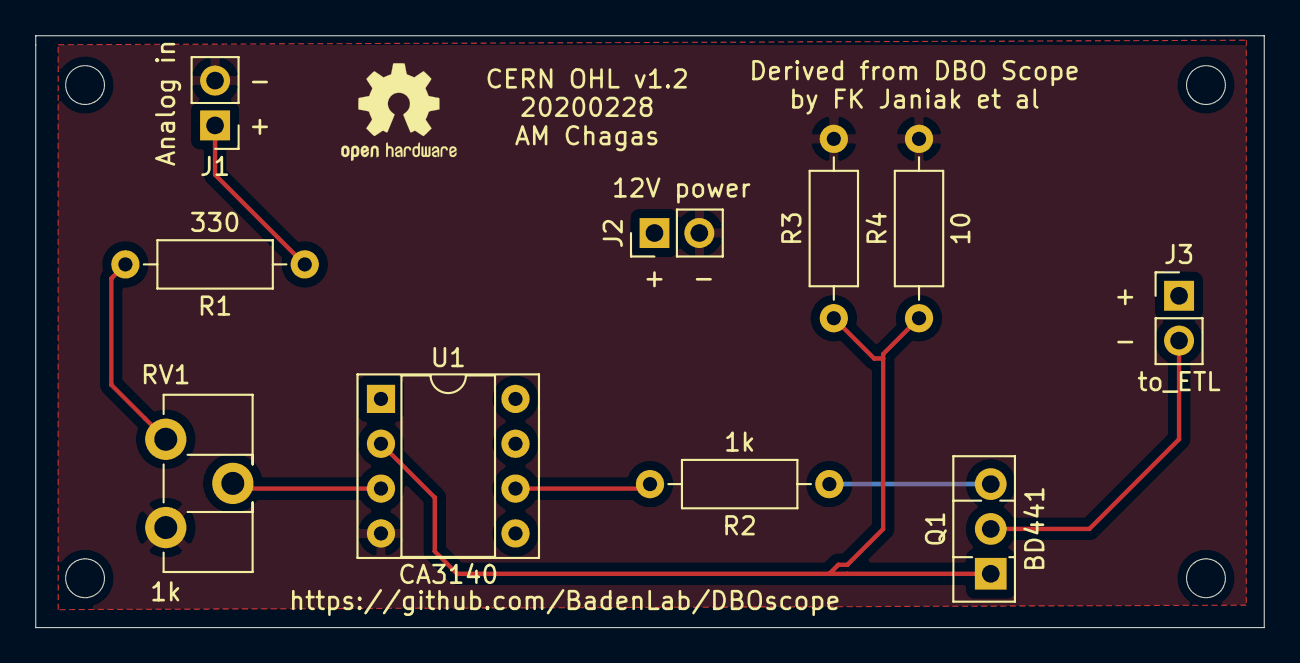
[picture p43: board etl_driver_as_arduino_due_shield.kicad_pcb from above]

Board: 2 copper layers, 69.6 x 33.5 mm, 10 parts (0 on the bottom side), 9 nets.

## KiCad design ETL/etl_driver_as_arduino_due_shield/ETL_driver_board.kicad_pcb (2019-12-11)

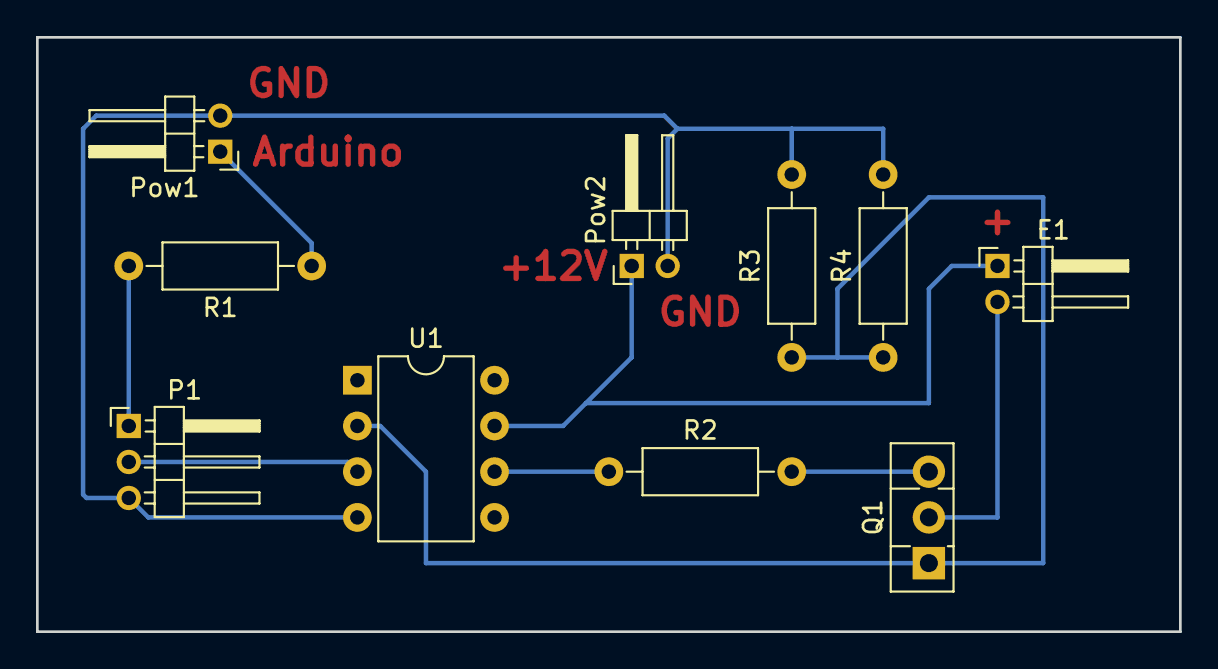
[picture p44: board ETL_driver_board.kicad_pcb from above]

Board: 2 copper layers, 63.5 x 33.0 mm, 10 parts (0 on the bottom side), 9 nets.

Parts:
E1: ETL; Pin_Header_Angled_1x02_Pitch2.00mm
P1: potentiometer; Pin_Header_Angled_1x03_Pitch2.00mm
Pow1: Pin_Header_Angled_1x02_Pitch2.00mm
Pow2: 12Vpower; Pin_Header_Angled_1x02_Pitch2.00mm
Q1: BD441; TO-126_Vertical
R1: 330; R_Axial_DIN0207_L6.3mm_D2.5mm_P10.16mm_Horizontal
R2: 1k; R_Axial_DIN0207_L6.3mm_D2.5mm_P10.16mm_Horizontal
R3, R4: 10; R_Axial_DIN0207_L6.3mm_D2.5mm_P10.16mm_Horizontal
U1: CA3140; DIP-8_W7.62mm

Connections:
GND: P1.3, Pow1.2, Pow2.2, R3.2, R4.2, U1.4
unnamed: E1.1, Pow2.1, U1.7
unnamed: E1.2, Q1.2
unnamed: P1.1, R1.2
unnamed: P1.2, U1.3
unnamed: Pow1.1, R1.1
unnamed: Q1.1, R3.1, R4.1, U1.2
unnamed: Q1.3, R2.2
unnamed: R2.1, U1.6

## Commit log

2019-10-27 Initial upload
    Preliminary user manual and BOM
    polished version + code etc coming soon
    [BOM (preliminary, polished version coming soon).xlsx]
2019-12-10 Prelim commit for manual update
    [ETL_driver_board.kicad_pcb, Lens_holder.stl]
2019-12-11 BOM update
    [BOM.xlsx]
2019-12-11 Clean up
    [BOM (preliminary, polished version coming soon).xlsx, ETL_driver_board.kicad_pcb, Lens_holder.stl]
2020-02-28 recreated PCB board in KiCad with proper production files, and started an arduino shield version
    [ETL_driver_board.kicad_pcb, etl_driver_as_arduino_due_shield.kicad_pcb, etl_driver_as_arduino_due_shield.sch, etl_driver_pcb-B_Adhes.gbr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]

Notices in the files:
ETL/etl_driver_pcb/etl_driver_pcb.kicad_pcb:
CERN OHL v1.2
